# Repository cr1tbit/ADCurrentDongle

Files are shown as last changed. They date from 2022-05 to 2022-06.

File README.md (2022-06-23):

# CurrentDongle attachment for the `Analog Discovery 2`

I actually use this simple board all the time, so decided to share it with the world.

It was made for these reasons:
* Simplifying current consumption measurement process, using AD2 bulit-in programmable voltage source, and dual INA186 amplifiers (for extended dynamic range)
* Breaking out BNC connectors, because, for some reason, such breakout board from Analog costs an ARM and a leg.
* Just breakout board for hacking stuff together

There's an simple bulit-in comparator circuit that blinks a LED when the channel range is reached. The high-accuracy channel usually also blinks when the DUT performs some action, which is also an useful feedback I guess.

In `scripts` folder, there's an example `digilent waveforms` script that I use for current measurement. Some things to note:
* programmable voltage sources on `AD2` are noisy as hell when the current is under a couple of milliamps - hence the resistor in this area.
* the voltage offset errors from `INA186`s can be easilly callibrated out, using the provided script.

What this device is NOT:
* Crosstalk-free oscilloscope adapter
* Super accurate, self calibrating current probe
* Lab-ready device

Stuff to improve:
* The LEDs will not work when system is powered by 1.8V - but it's not fixable easily.

## Some pics:

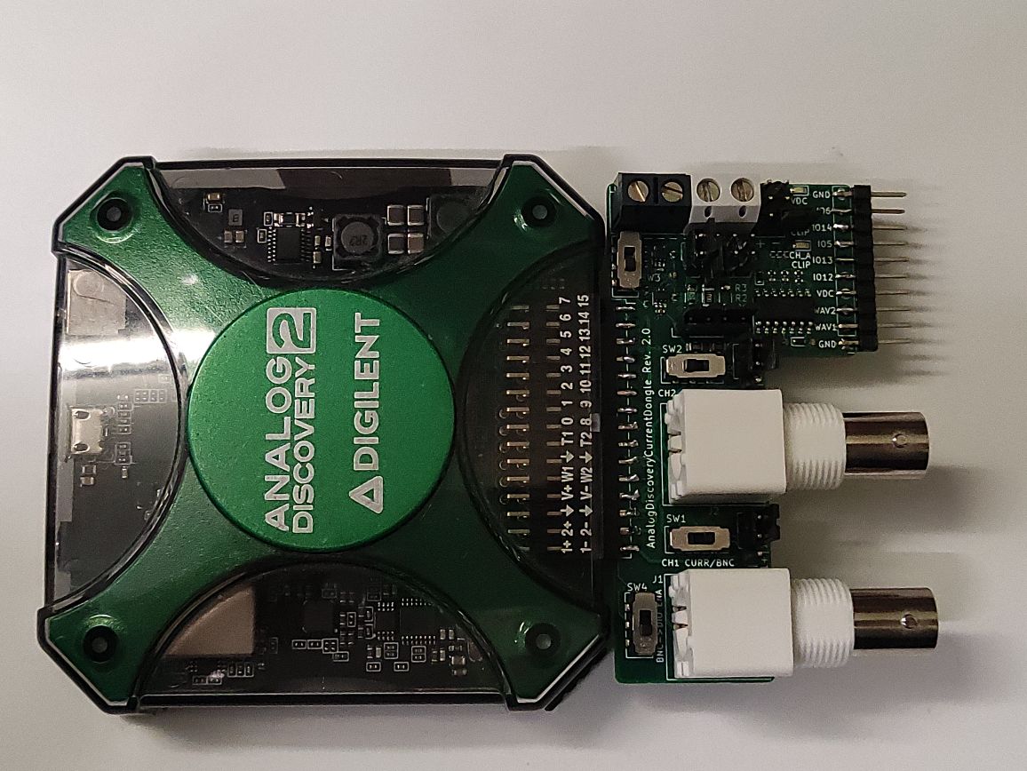
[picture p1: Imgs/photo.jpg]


PCB connected to the Analog Discovery 2

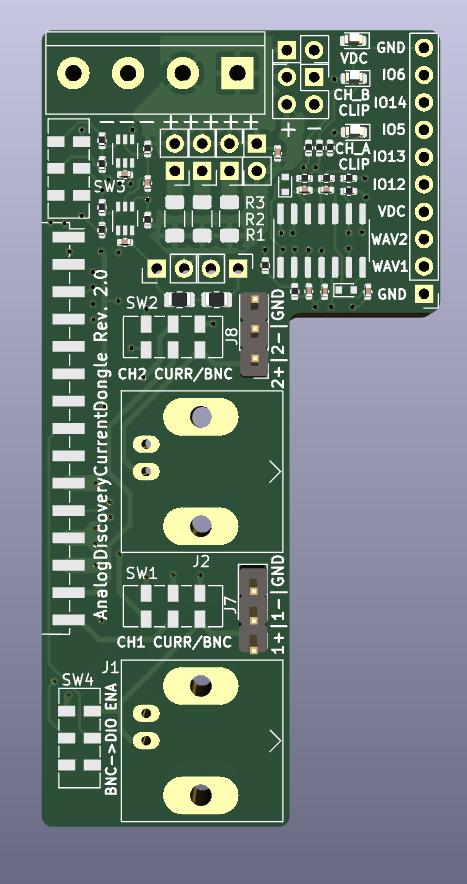
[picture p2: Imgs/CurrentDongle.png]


PCB render

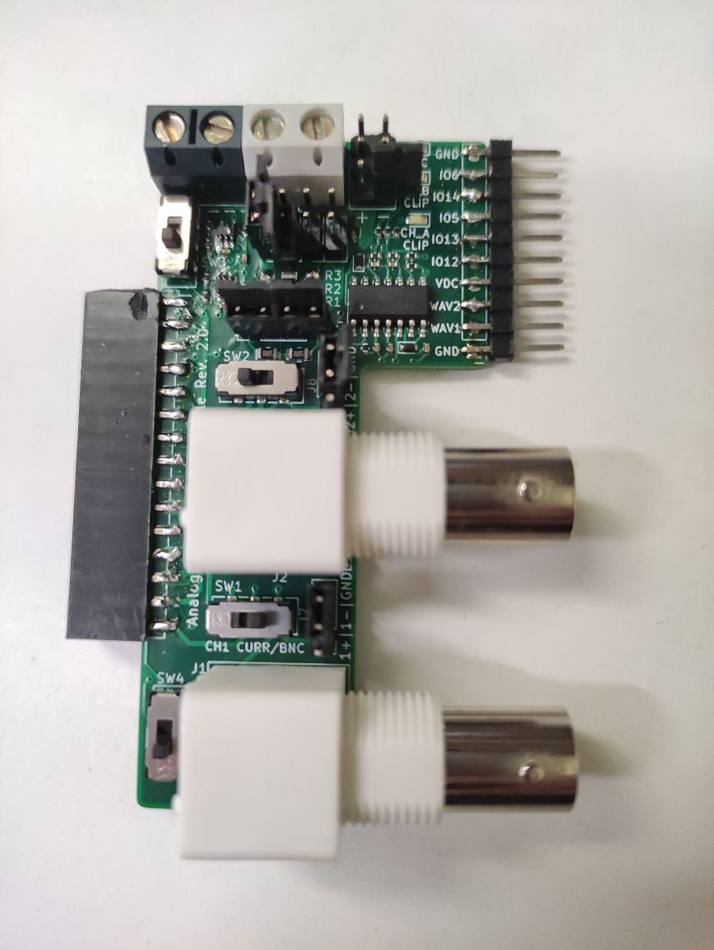
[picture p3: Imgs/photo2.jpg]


PCB IRL

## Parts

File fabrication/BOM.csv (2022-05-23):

Comment | Designator | Footprint | LCSC
100n | C1,C3,C4,C7 | Capacitor_SMD:C_0402_1005Metric
22n | C2,C5,C6,C8,C9 | Capacitor_SMD:C_0402_1005Metric | C1532
1N4148WT | D1,D2 | Diode_SMD:D_SOD-523
LED | D3,D4,D5 | LED_SMD:LED_0603_1608Metric | C2290
5/0.1% | R1 | Resistor_SMD:R_1206_3216Metric_Pad1.30x1.75mm_HandSolder
100k | R11,R14,R15 | Resistor_SMD:R_0402_1005Metric
1Meg | R12,R13 | Resistor_SMD:R_0402_1005Metric
50 | R18,R19 | Resistor_SMD:R_0805_2012Metric
1/0.1% | R2 | Resistor_SMD:R_1206_3216Metric_Pad1.30x1.75mm_HandSolder | C17928
0.2/0.1% | R3 | Resistor_SMD:R_1206_3216Metric_Pad1.30x1.75mm_HandSolder | C25336
100 | R4,R5 | Resistor_SMD:R_0402_1005Metric
330 | R6,R8 | Resistor_SMD:R_0402_1005Metric
3k3 | R7,R9,R10,R16,R17,R20 | Resistor_SMD:R_0402_1005Metric
SWITCHES | SW1,SW2, SW3, SW4 | Button_Switch_SMD:SW_DPDT_CK_JS202011JCQN | C221665
INA186AxDDxx | U1,U2 | Package_TO_SOT_SMD:Texas_R-PDSO-G6
MCP6004 | U3 | Package_SO:SOIC-14_3.9x8.7mm_P1.27mm

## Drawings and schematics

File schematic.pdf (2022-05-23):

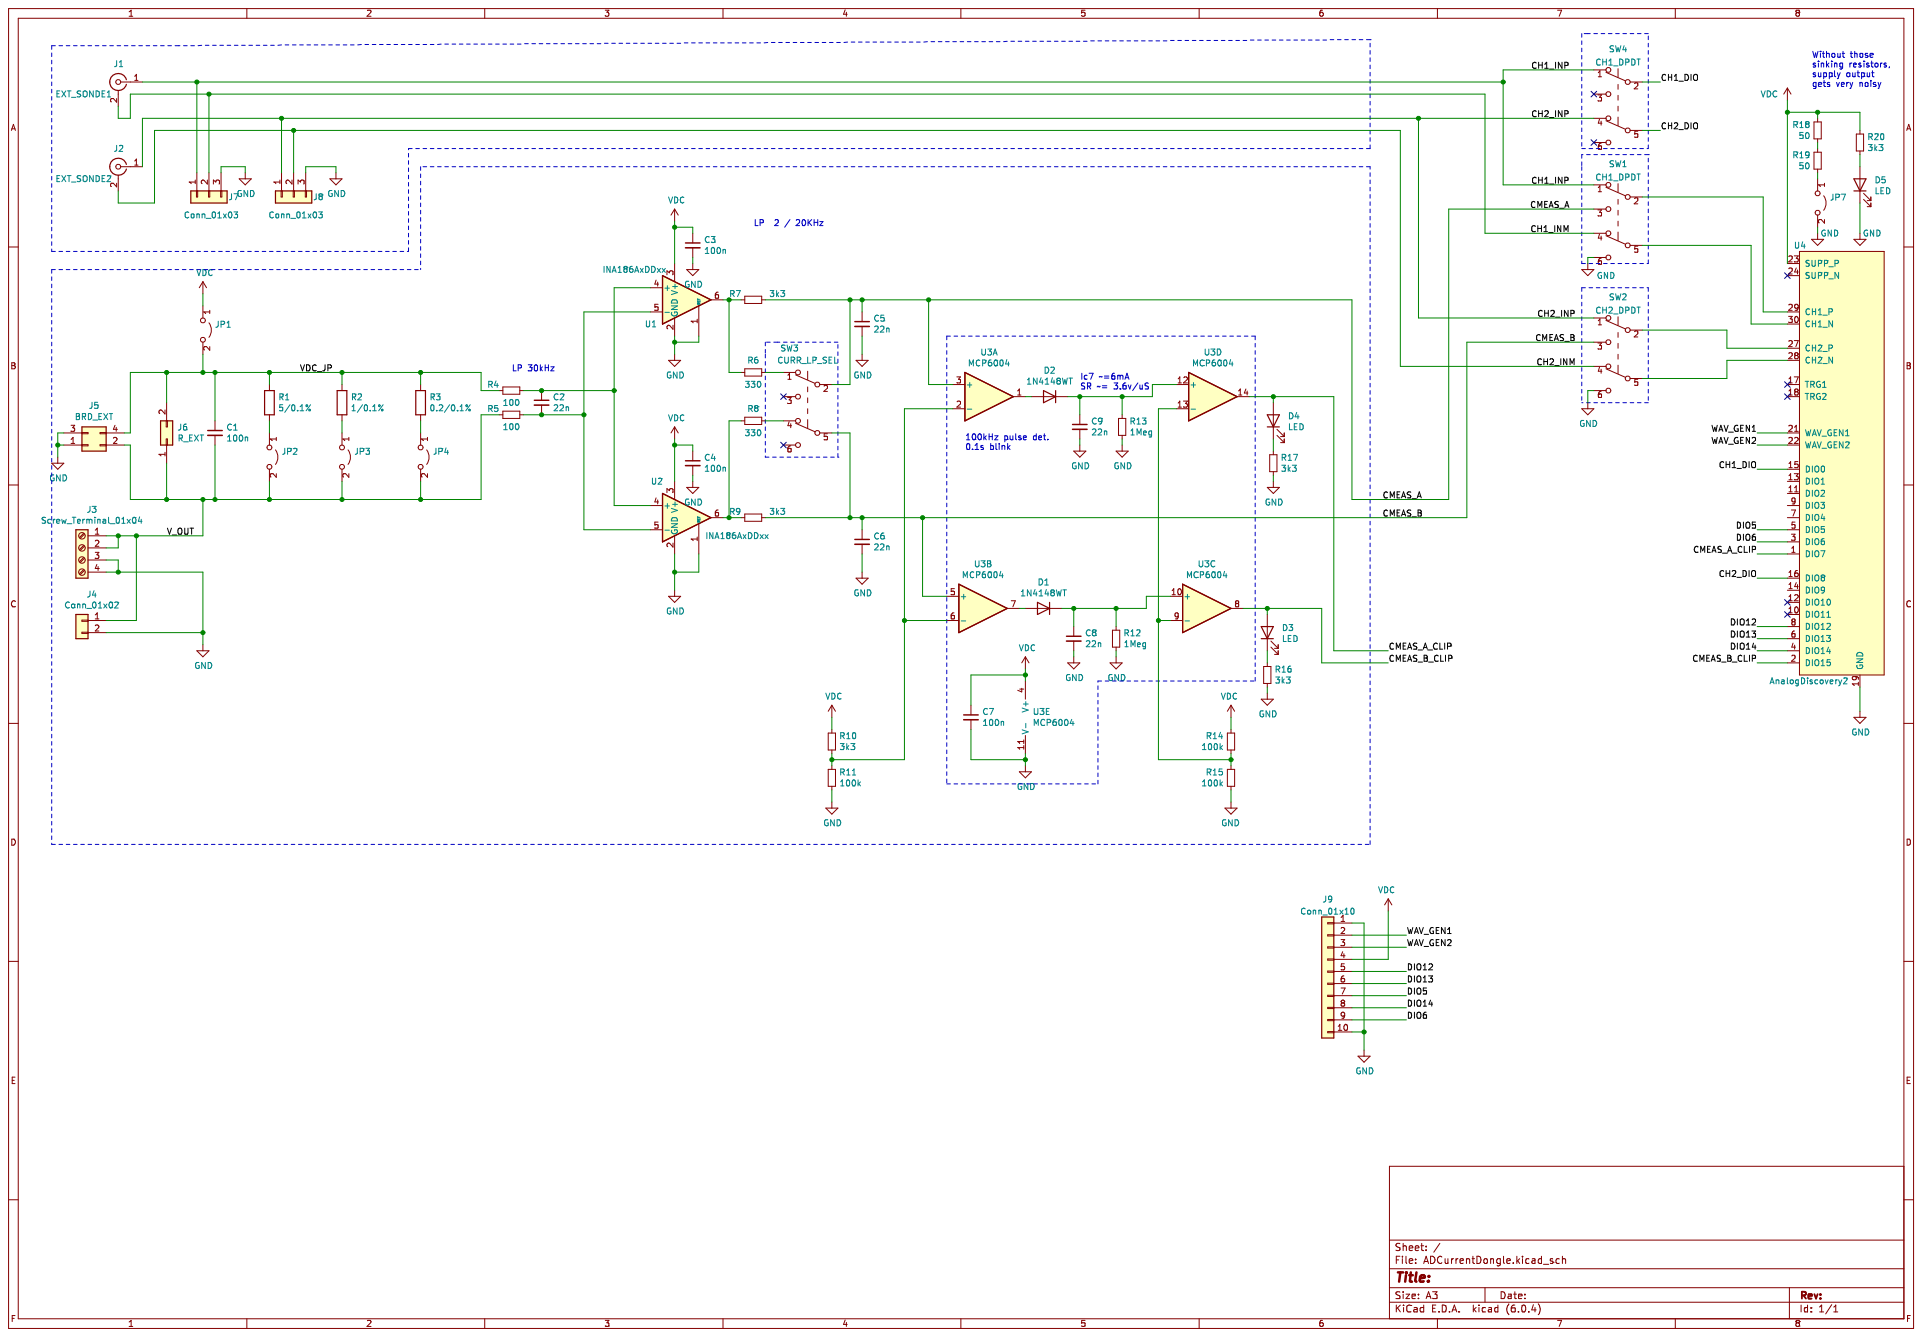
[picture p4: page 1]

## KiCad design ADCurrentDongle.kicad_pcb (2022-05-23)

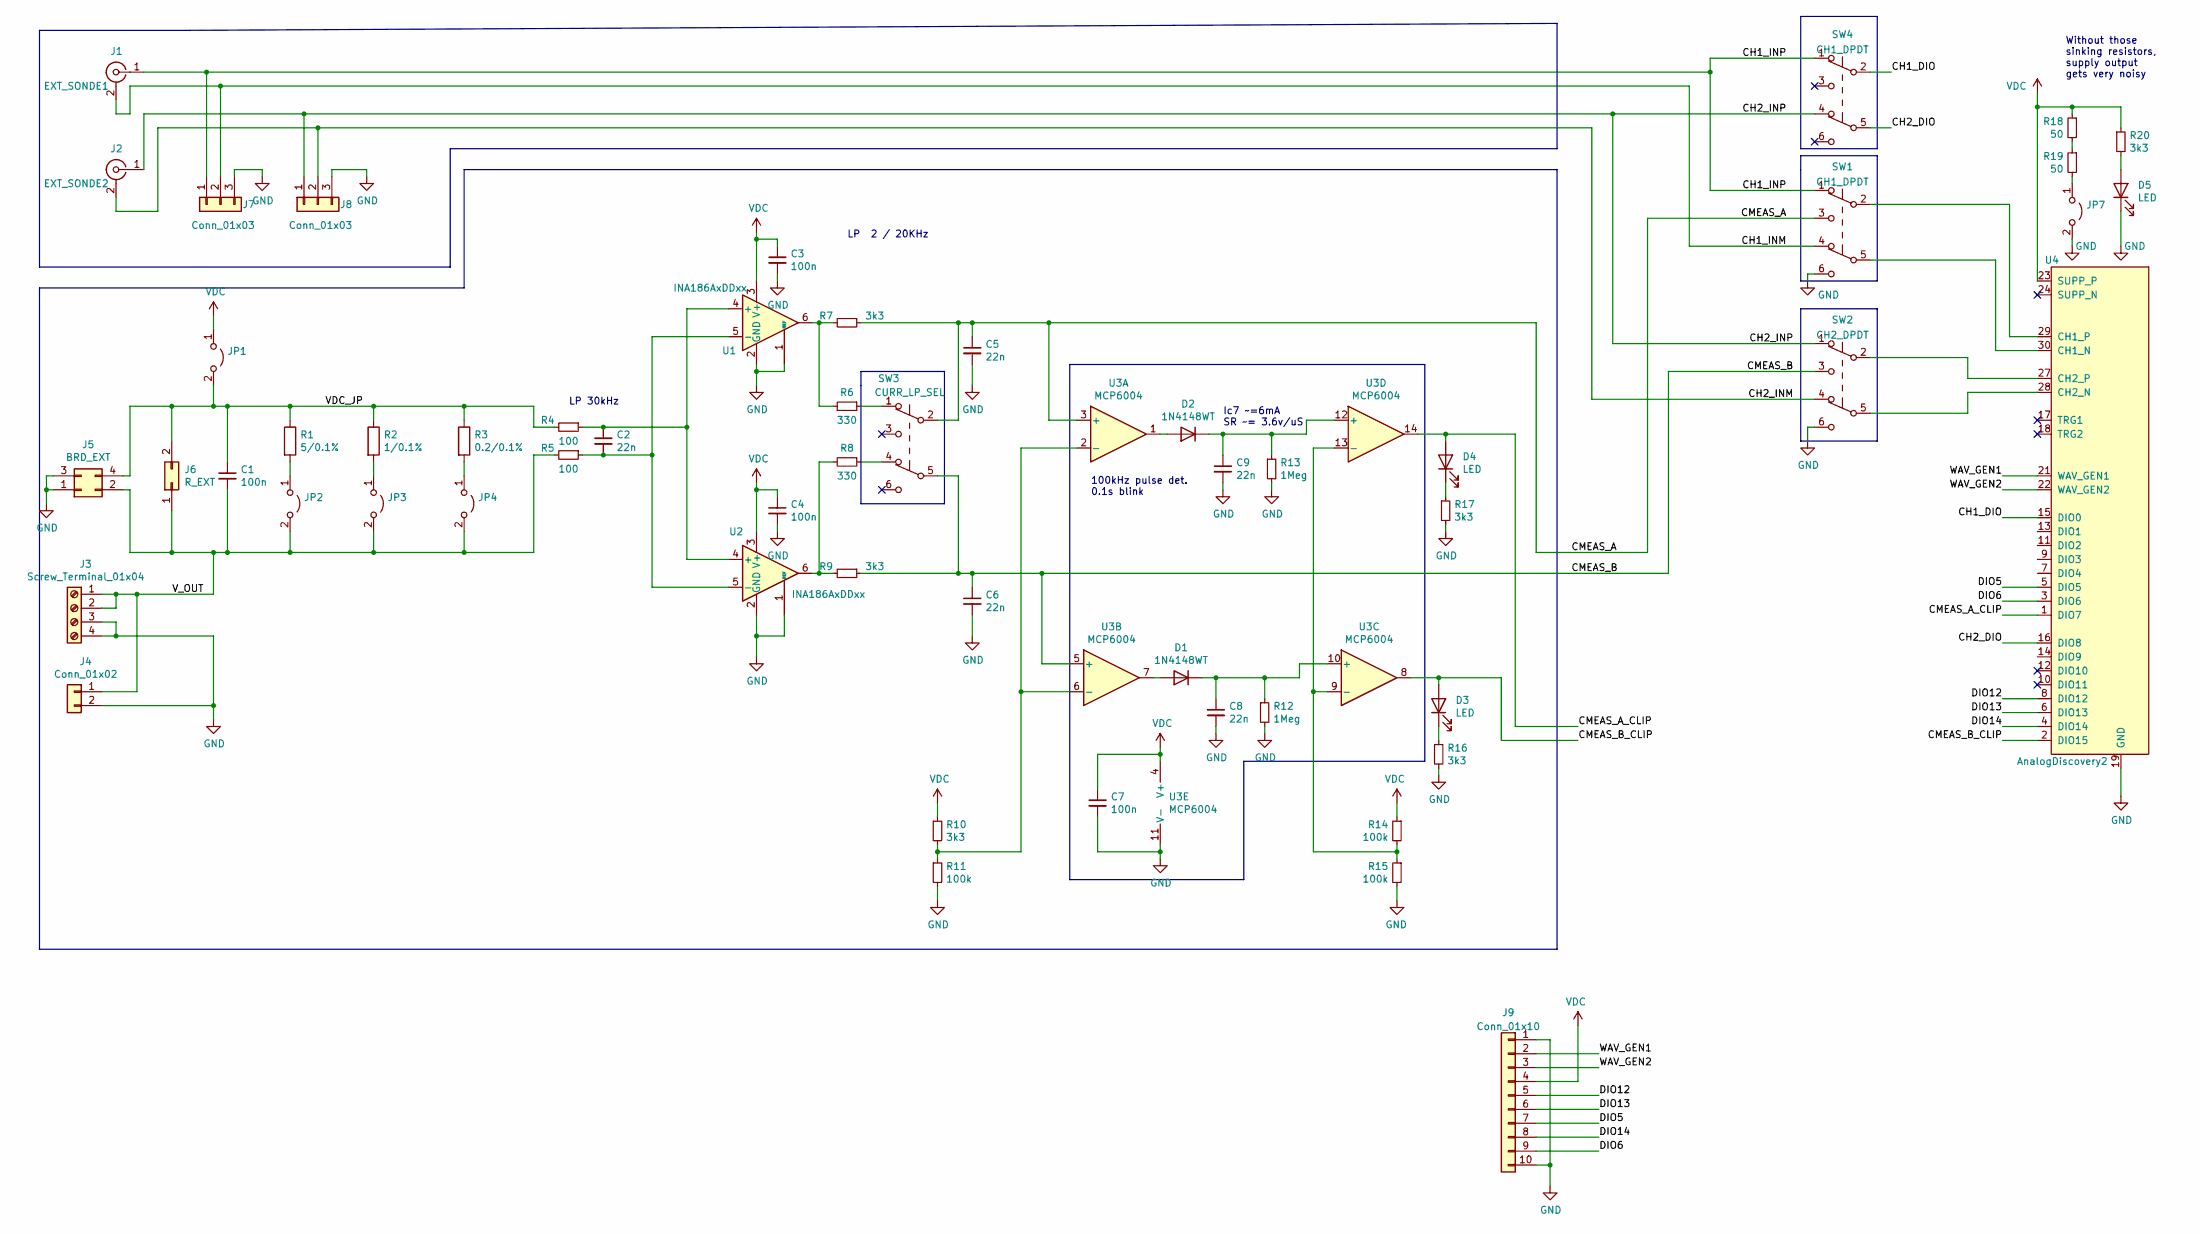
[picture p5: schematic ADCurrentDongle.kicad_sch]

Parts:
C1, C3, C4, C7: 100n; C_0402_1005Metric
C2, C5, C6, C8, C9: 22n; C_0402_1005Metric
D1, D2: 1N4148WT; D_SOD-523
D3, D4, D5: LED; LED_0603_1608Metric
J1: EXT_SONDE1; BNC_Amphenol_B6252HB-NPP3G-50_Horizontal
J2: EXT_SONDE2; BNC_Amphenol_B6252HB-NPP3G-50_Horizontal
J3: Screw_Terminal_01x04; TerminalBlock_bornier-4_P5.08mm
J4: Conn_01x02; PinHeader_1x02_P2.54mm_Vertical
J5: BRD_EXT; PinSocket_2x02_P2.54mm_Vertical
J6: R_EXT; PinHeader_1x02_P2.54mm_Vertical
J7, J8: Conn_01x03; PinHeader_1x03_P2.54mm_Vertical
J9: Conn_01x10; PinHeader_1x10_P2.54mm_Vertical
JP1, JP2, JP3, JP4, JP7: Jumper_2_Open; PinHeader_1x02_P2.54mm_Vertical
R1: 5/0.1%; R_1206_3216Metric_Pad1.30x1.75mm_HandSolder
R2: 1/0.1%; R_1206_3216Metric_Pad1.30x1.75mm_HandSolder
R3: 0.2/0.1%; R_1206_3216Metric_Pad1.30x1.75mm_HandSolder
R4, R5: 100; R_0402_1005Metric
R6, R8: 330; R_0402_1005Metric
R7, R9, R10, R16, R17, R20: 3k3; R_0402_1005Metric
R11, R14, R15: 100k; R_0402_1005Metric
R12, R13: 1Meg; R_0402_1005Metric
R18, R19: 50; R_0805_2012Metric
SW1, SW4: CH1_DPDT; SW_DPDT_CK_JS202011JCQN
SW2: CH2_DPDT; SW_DPDT_CK_JS202011JCQN
SW3: CURR_LP_SEL; SW_DPDT_CK_JS202011JCQN
U1, U2: INA186AxDDxx; Texas_R-PDSO-G6
U3: MCP6004; SOIC-14_3.9x8.7mm_P1.27mm
U4: AnalogDiscovery2; AnalogDiscovery2_side_con

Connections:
/CH1_DIO: SW4.2 (B), U4.15 (DIO0)
/CH1_INM: J1.2 (Ext), J7.2, SW1.4 (A)
/CH1_INP: J1.1 (In), J7.1, SW1.1 (A), SW4.1 (A)
/CH2_DIO: SW4.5 (B), U4.16 (DIO8)
/CH2_INM: J2.2 (Ext), J8.2, SW2.4 (A)
/CH2_INP: J2.1 (In), J8.1, SW2.1 (A), SW4.4 (A)
/CMEAS_A: C5.1, R7.1, SW1.3 (C), SW3.2 (B), U3.3 (+)
/CMEAS_A_CLIP: D4.2 (A), U3.14, U4.1 (DIO7)
/CMEAS_B: C6.1, R9.1, SW2.3 (C), SW3.5 (B), U3.5 (+)
/CMEAS_B_CLIP: D3.2 (A), U3.8, U4.2 (DIO15)
/DIO5: J9.7, U4.5 (DIO5)
/DIO6: J9.9, U4.3 (DIO6)
/DIO12: J9.5, U4.8 (DIO12)
/DIO13: J9.6, U4.6 (DIO13)
/DIO14: J9.8, U4.4 (DIO14)
/VDC_JP: C1.1, J5.4, J6.2, JP1.2 (B), R1.1, R2.1, R3.1, R4.2
/V_OUT: C1.2, J3.1, J3.2, J4.1, J5.2, J6.1, JP2.2 (B), JP3.2 (B), JP4.2 (B), R5.2
/WAV_GEN1: J9.2, U4.21 (WAV_GEN1)
/WAV_GEN2: J9.3, U4.22 (WAV_GEN2)
GND: C3.2, C4.2, C5.2, C6.2, C7.2, C8.2, C9.2, D5.1 (K), J3.3, J3.4, J4.2, J5.1, J5.3, J7.3, J8.3, J9.1, J9.10, JP7.2 (B), R11.2, R12.2, R13.2, R15.2, R16.2, R17.2, SW1.6 (C), SW2.6 (C), U1.1 (REF), U1.2 (GND), U2.1 (REF), U2.2 (GND), U3.11 (V-), U4.19 (GND), U4.20 (GND), U4.25 (GND), U4.26 (GND)
unnamed: C2.1, R4.1, U1.4 (+), U2.4 (+)
unnamed: C2.2, R5.1, U1.5 (-), U2.5 (-)
unnamed: C8.1, D1.1 (K), R12.1, U3.10 (+)
unnamed: C9.1, D2.1 (K), R13.1, U3.12 (+)
unnamed: D1.2 (A), U3.7
unnamed: D2.2 (A), U3.1
unnamed: D3.1 (K), R16.1
unnamed: D4.1 (K), R17.1
unnamed: JP2.1 (A), R1.2
unnamed: JP3.1 (A), R2.2
unnamed: JP4.1 (A), R3.2
unnamed: JP7.1 (A), R19.2
unnamed: R6.1, SW3.1 (A)
unnamed: R6.2, R7.2, U1.6
unnamed: R8.1, SW3.4 (A)
unnamed: R8.2, R9.2, U2.6
unnamed: R10.2, R11.1, U3.2 (-), U3.6 (-)
unnamed: R14.2, R15.1, U3.9 (-), U3.13 (-)
unnamed: R18.2, R19.1
unnamed: D5.2 (A), R20.2
unnamed: SW1.2 (B), U4.29 (CH1_P)
unnamed: SW1.5 (B), U4.30 (CH1_N)
unnamed: SW2.2 (B), U4.27 (CH2_P)
unnamed: SW2.5 (B), U4.28 (CH2_N)
VDC: C3.1, C4.1, C7.1, J9.4, JP1.1 (A), R10.1, R14.1, R18.1, R20.1, U1.3 (V+), U2.3 (V+), U3.4 (V+), U4.23 (SUPP_P)

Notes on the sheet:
LP 30kHz
Ic7 ~=6mA SR ~= 3.6v/uS
LP 2 / 20KHz
Without those sinking resistors, supply output gets very noisy
100kHz pulse det. 0.1s blink

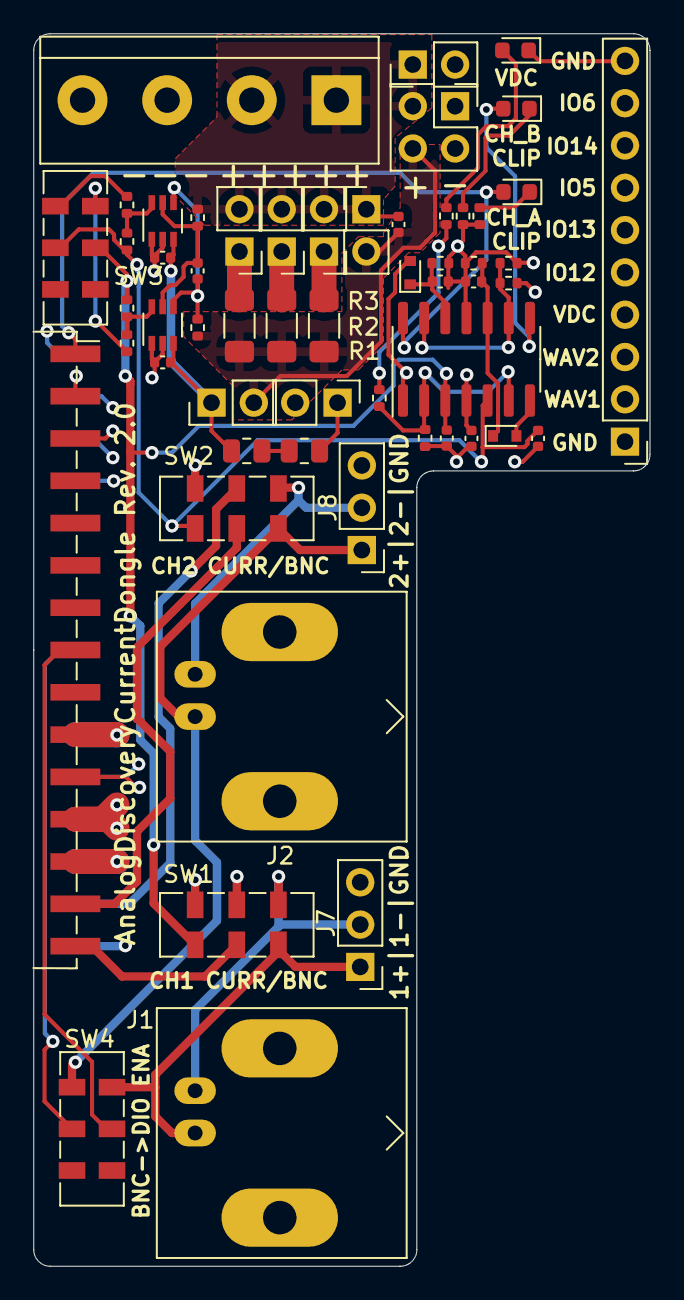
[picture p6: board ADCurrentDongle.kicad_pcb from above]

Board: 4 copper layers, 37.0 x 74.0 mm, 56 parts (0 on the bottom side), 45 nets.

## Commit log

2021-06-25 gityfying the repo
    [analog-discovery-current-meas-job.gbrjob, analog-discovery-current-meas.kicad_pcb, analog-discovery-current-meas.sch]
2021-06-26 renaming project
    [ADCurrentDongle.kicad_pcb, ADCurrentDongle.sch]
2022-02-27 commiting WIP in hope of catching a routing bug
    [ADCurrentDongle.kicad_pcb, ADCurrentDongle.kicad_sch]
2022-03-11 adding new rev fabrication and stuff
    [ADCurrentDongle.kicad_pcb, ADCurrentDongle.kicad_sch, analog-discovery-current-meas-job.gbrjob]
2022-05-20 pre order commit
    [ADCurrentDongle.kicad_pcb, ADCurrentDongle.kicad_sch]
2022-05-23 fabrication outputs
    [ADCurrentDongle.kicad_pcb, ADCurrentDongle.kicad_sch, BOM.csv, analog-discovery-current-meas-job.gbrjob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]
